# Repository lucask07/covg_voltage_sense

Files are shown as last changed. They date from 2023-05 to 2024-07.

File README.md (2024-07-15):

# COVG Voltage Sense Board

This board is physically small so it can be housed in an enclosure on a micromanipulator. The board input is a BNC connector which is compatible with glass microelectrode holders. 

The input amplifier must have low capacitance to minimize the total filter from the capacitance and the microelectrode resistance. The first version has a fixed amplifier gain. 

The **Rev_b board** modifications were designed and implemented by undergraduate student Jordan Haag. The board incorporates programmable gain and uses a low-noise voltage reference, REF3440, as the reference input to the offset adjust DAC. The low-noise reference improves the noise performance of the system. 

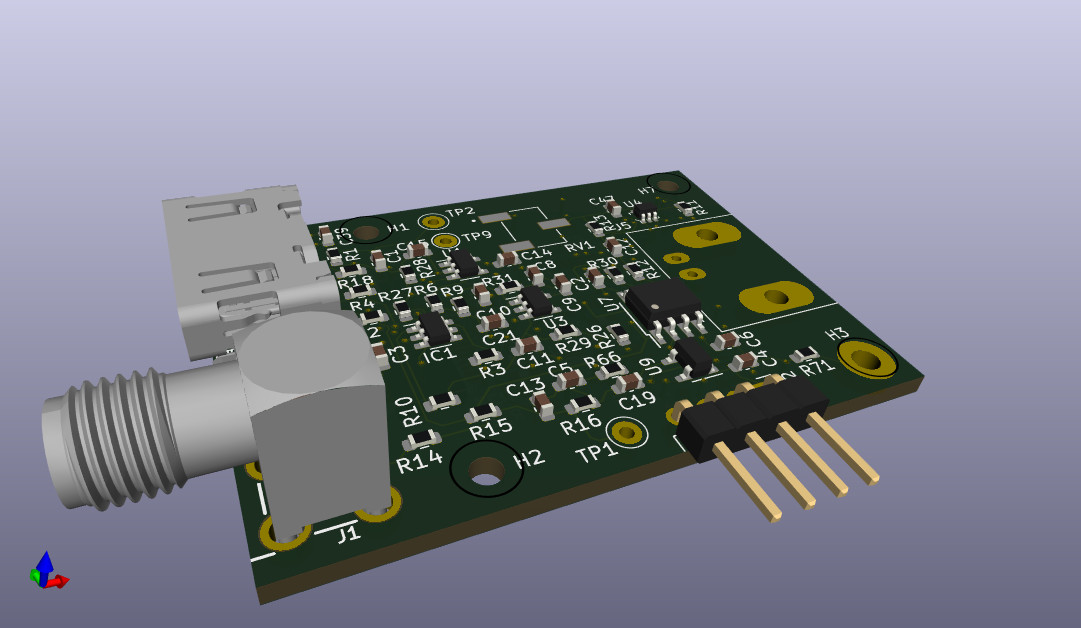
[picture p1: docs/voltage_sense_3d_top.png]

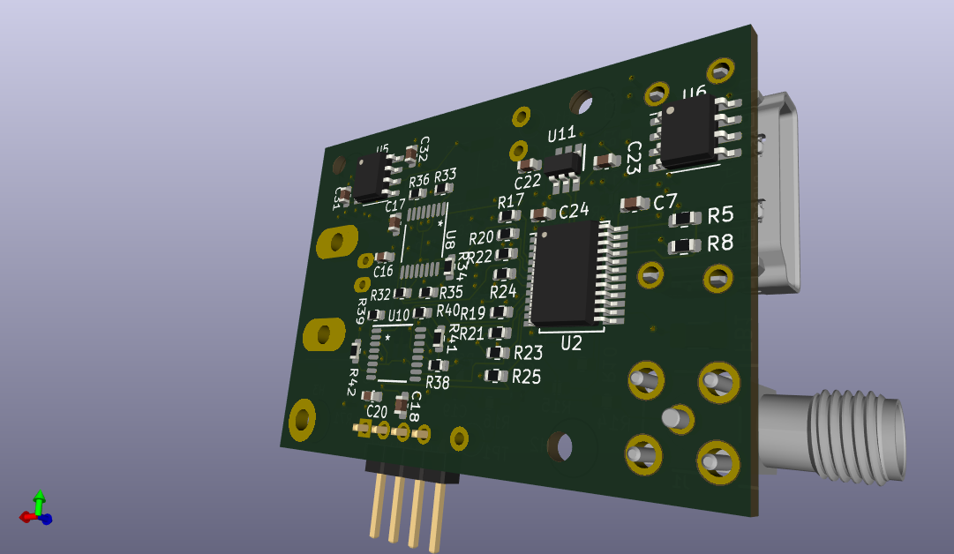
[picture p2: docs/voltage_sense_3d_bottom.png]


## Schematic
The [schematic](docs/voltage_sense.pdf) is in the DOCS folder.

## Fabrication
The second revision of this board was fabricated and assembled by JLCPCB. 

Order #: Y13-3276043A 

Assembly: SMT02402281623205-3276043A

Date: 2024/02/29

## Bill of Materials

The BOM is here JLCPCB assembly BOM 

Certain parts are not directly available from LCSC and so were pre-ordered. Pre-order: 24AA025UID, OPA1641,
DAC101C081CIMK/NOPB, TMUX6111PWR, TCA9555DBR, LP2981A-33DBVT, ADA4000-2ARZ-R7. Global sourcing: 3269W-1-103GLF, REF3440TIDBVR.

## Bugs and Future Improvement

* A footprint for a capacitor should be included in parallel with the feedback gain resistors, for example R33, R34, R35, and R36. This limits the amplifier bandwidth. Currently we work around this omission by stacking a capacitor on top of the resistor. Issue ([#4][i4])

[i4]: https://github.com/lucask07/covg_voltage_sense/issues/4

* U8,U10 (TMUX6111) and U11 (REF3440) were not assembled by JLCPCB and were lated added by hand.

## Upgrades 

This version addresses the following issues that occured with V1 

* DAC reference noise: https://github.com/lucask07/covg_voltage_sense/issues/5
* Negative capacitance connection: https://github.com/lucask07/covg_voltage_sense/issues/3
* C8 causes oscillation: https://github.com/lucask07/covg_voltage_sense/issues/2
* Incorrect BOM resistor values: https://github.com/lucask07/covg_voltage_sense/issues/1

## Miscellaneous

### HDMI: connection from DAQ to daughtercard 

The digital COVG project uses the concept of one main data acquisition board connected to an FPGA. The main data acquisition board has multiple channels that extend to daughtercards. The connection to each daughtercard allows for low-latency control by connections to high-speed ADCs and DACs on the daq board. For COVG the daughtercards are the bath clamp; the guard clamp; the voltage clamp and I force; and the V1/V2. The connectivity to the daughtercard is generalized and will be the same for each. 

An HDMI-A cable is used for input and output signals that connect the bath clamp daughtercard to the DAQ board. The HDMI cable carries:

- **power**: +5V, +15V, -15V
- **GND** 
- **Analog outputs** (to ADCs): 
	- OUT\_P, OUT\_N differential pair (x1) to 5 MSPS ADC 
	- single-ended out AMP\_OUT, CAL\_ADC both to individual channel of 1 MSPS ADC (ADS8686) 
- **Analog reference**: VCM: buffered ADC common-mode voltage (nominal 2.5 V)
- **Digital inputs** (from DACs): 
	- CMD: (command signal) from 1 us settling time DAC (attenuated by x10 at board)
	- CC: (capacitive compensation) from 1 us settling time DAC. AC coupled. 
	- CAL_DAC: from 5 us settling time DAC (DAC8050). Either voltage source or current source (Howland current pump), programmable on DAQ board
- **Digital control** (I2C): SDA, SCL (@ 3.3 V levels). Pull-ups are on DAQ board not on the daughtercards! The daughtercards use a TCA9555 I/O expander to generate many control signals from the I2C interface. 
- **Utiility** grab-bag connected to test-point. Jumper on DAQ board to set to analog in, analog out or digital I/O.

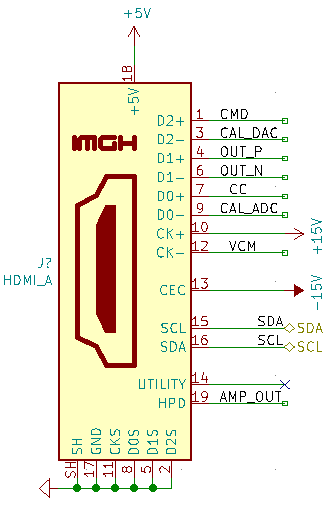
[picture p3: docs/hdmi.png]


| Pin | HDMI name    | Generic Daughtercard     | Bath clamp | Notes  |
|-----|--------------|--------------|------------|---------------------------------------------------------------------------|
| 1   | Data2+       | fastDAC1     | CMD        | ~1 us settling time                      |
| 2   | Data2 shield | Gnd          | Gnd        |                                                                           |
| 3   | Data2-       | Analog/GPIO1 | CAL_DAC    | Analog input signal from DAC8050, 16 bit, 5us settle, 5 V supply                                                                         |
| 4   | Data1+       | fastADC+     | IM_P       | to AD7960/AD7961. Differential low-pass filter on DAQ board                                                                          |
| 5   | Data1 shield | Gnd          | Gnd        |                                                                           |
| 6   | Data1-       | fastADC-     | IM_N       | to AD7960/AD7961. Differential low-pass filter on DAQ board                                                                          |
| 7   | Data0+       | fastDAC2     | CC         | ~1 us settling time                                                                          |
| 8   | Data0 shield | Gnd          | Gnd        |                                                                           |
| 9   | Data0-       | Analog/GPIO2 | CAL_ADC    | to ADS8686 1 MSPS, programmable PGA for range up to +/-10V                                                           |
| 10  | Clock+       | 15V          | 15V        | From a linear regulator on the DAQ board, 75 mA max per channel                                                                         |
| 11  | Clock shield | Gnd          | Gnd        |                                                                           |
| 12  | Clock-       | VCM          | VCM        | buffered on DAQ board, nominal 2.5 V                                                                          |
| 13  | CEC          | -15V         | -15V       | From a linear regulator on the DAQ board, 75 mA max per channel                             |
| 14  | Reserved     | open         | open       | Resistor jumper on DAQ board sets as analog in, analog out, or digital I/O (@ 3.3 V levels). Default stuffing option is to connect to the general purpose ADC (ADS8686). |
| 15  | SCL          | SCL          | SCL        | I2C clock. Pull-up on main DAQ board, 3.3 V levels                |
| 16  | SDA          | SDA          | SDA        | I2C data. Pull-up on main DAQ board, 3.3 V levels                 |
| 17  | Gnd          | Gnd          | Gnd        |                                                                           |
| 18  | 5V           | 5V           | 5V         | Power input from linear regulator, 200 mA max per channel (target)  |
| 19  | HPD          | Analog/GPIO3 | AMP_OUT    | output to ADS8686 1 MSPS, programmable PGA                        |

### Acknowledgments

Research reported in this repository was supported by the National Institute Of Neurological Disorders And Stroke of the National Institutes of Health under Award Number R15NS116907. The content is solely the responsibility of the authors and does not necessarily represent the official views of the National Institutes of Health.

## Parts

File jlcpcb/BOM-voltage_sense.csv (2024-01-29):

Comment | Designator | Footprint | LCSC
1n | C8 | C_0603_1608Metric | C100040
10p | C21 | C_0603_1608Metric | C106245
1u | C11,C23,C24 | C_0603_1608Metric | C106858
470k | R35,R41 | R_0603_1608Metric | C114622
33R | R14,R18 | R_0603_1608Metric | C13320
3k | R1,R11,R13,R16,R26,R30 | R_0603_1608Metric | C137732
OPA188xxDBV | U1,U3 | TSOT-23-5 | C140312
100k | R17,R19,R20,R21,R22,R23,R24,R25,R5 | R_0603_1608Metric | C14675
0.1u | C10,C14,C15,C16,C17,C18,C2,C20,C22,C3,C31,C32,C39,C4,C47,C6,C7,C9 | C_0603_1608Metric | C1591
10p | C12 | C_0603_1608Metric | C1634
Ferrite_Bead | FB1 | C_1206_3216Metric | C16902
24AA025UID | U6 | SOIC-8_3.9x4.9mm_P1.27mm | C194184
OPA1641 | U5 | SOIC-8_3.9x4.9mm_P1.27mm | C2057597
0R | R12,R71 | R_0603_1608Metric | C21189
348k | R34,R40 | R_0603_1608Metric | C227488
226k | R33,R39 | R_0603_1608Metric | C227714
30k | R15,R2 | R_0603_1608Metric | C22984
604k | R36,R42 | R_0603_1608Metric | C245986
1R | R66 | R_0603_1608Metric | C25212
Conn_Coaxial | J5 | BNC_Amphenol_B6252HB-NPP3G-50_Horizontal | C2837587
LP2981A-33DBVT | U9 | SOT-23-5 | C2872227
Conn_Coaxial | J1 | BU-SMA-G | C2874827
HDMI_A | J4 | CONN_10029449-111RLF_HDMI_A | C427307
MCP4017T-103E_LT | U4 | SOT-363 | C478095
4.7u | C5 | C_0603_1608Metric | C69335
49.9k | R10,R6 | R_0603_1608Metric | C705780
4.99k | R29,R9 | R_0603_1608Metric | C723532
49.9R | R31 | R_0603_1608Metric | C859049
10k | R27,R28,R3 | R_0603_1608Metric | C95204
DNI | R8 | R_0603_1608Metric
DNI | R4 | R_0603_1608Metric
DNI | H3 | MountingHole_2.2mm_M2_Pad
DNI | H7 | MountingHole_2.2mm_M2
DNI | J2 | PinHeader_1x04_P2.54mm_Horizontal
TCA9555DBR | U2 | SSOP-24_5.3x8.2mm_P0.65mm
DNI | C1 | C_0603_1608Metric
RCT-0C | TP1,TP2 | Test_Point_D1.02mm
DNI | C19 | C_0603_1608Metric
DAC101C081CIMK_NOPB | IC1 | TSOT-23-6
DNI | TP9 | TestPoint_THTPad_D2.0mm_Drill1.0mm
DNI | H1 | MountingHole_2.2mm_M2
10k pot | RV1 | TRIM_3269W-1-103GLF
DNI | C13 | C_0603_1608Metric
DNI | H2 | MountingHole_2.2mm_M2
ADA4000-2ARZ-R7 | U7 | R_8_ADI
TMUX6111PWR | U10 | PW0016A_N
DNI | R32 | R_0603_1608Metric
DNI | R38 | R_0603_1608Metric
TMUX6111PWR | U8 | PW0016A_N
REF3440TIDBVR | U11 | REF3440

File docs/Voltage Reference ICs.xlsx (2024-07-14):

Package | Manf # | DigiKey # | Price ($) | Quantity in Stock | LCSC Stock? | Noise Voltage at 10 Hz(uV p-p) | Noise Voltage at 10k Hz(uV p-p) | Accuracy (%) | Notes
SOT-6 | MAX6071BAUT41+T | MAX6071BAUT41+TCT-ND | 3 | 11000 | N | 9.6 | 34 | 0.08 | pin compatible w/same bypass caps
SOT-6 | REF3440TIDBVR | 296-REF3440TIDBVRCT-ND | 2.54 | 1800 | N | 3.8 | 48 | 0.05 | pin compatible w/same bypass caps
8-SO | LTC1798CS8-4.1#PBF | 505-LTC1798CS8-4.1#PBF-ND | 6.37 | 100 | N | 8 | - | 0.15 | not pin compatible
8-SOIC | LM4140BCM-4.1/NOPB | LM4140BCM-4.1/NOPB-ND | 5.77 | 540 | N | 2.2 | - | 0.1 | not pin compatible
8-VSSOP | REF3440QDGKRQ1 | 296-REF3440QDGKRQ1CT-ND | 3.8 | 2500 | N | 3.8 | 48 | 0.05 | not pin compatible
8-MSOP | LTC1258CMS8-4.1#PBF | 505-LTC1258CMS8-4.1#PBF-ND | 7.28 | 110 | N | 8 | - | 0.18 | not pin compatible
8-MSOP | ADR444ARMZ-REEL7 | 505-ADR444ARMZ-REEL7CT-ND | 8.37 | 1200 | Y | 1.8 | - | 0.13 | not pin compatible

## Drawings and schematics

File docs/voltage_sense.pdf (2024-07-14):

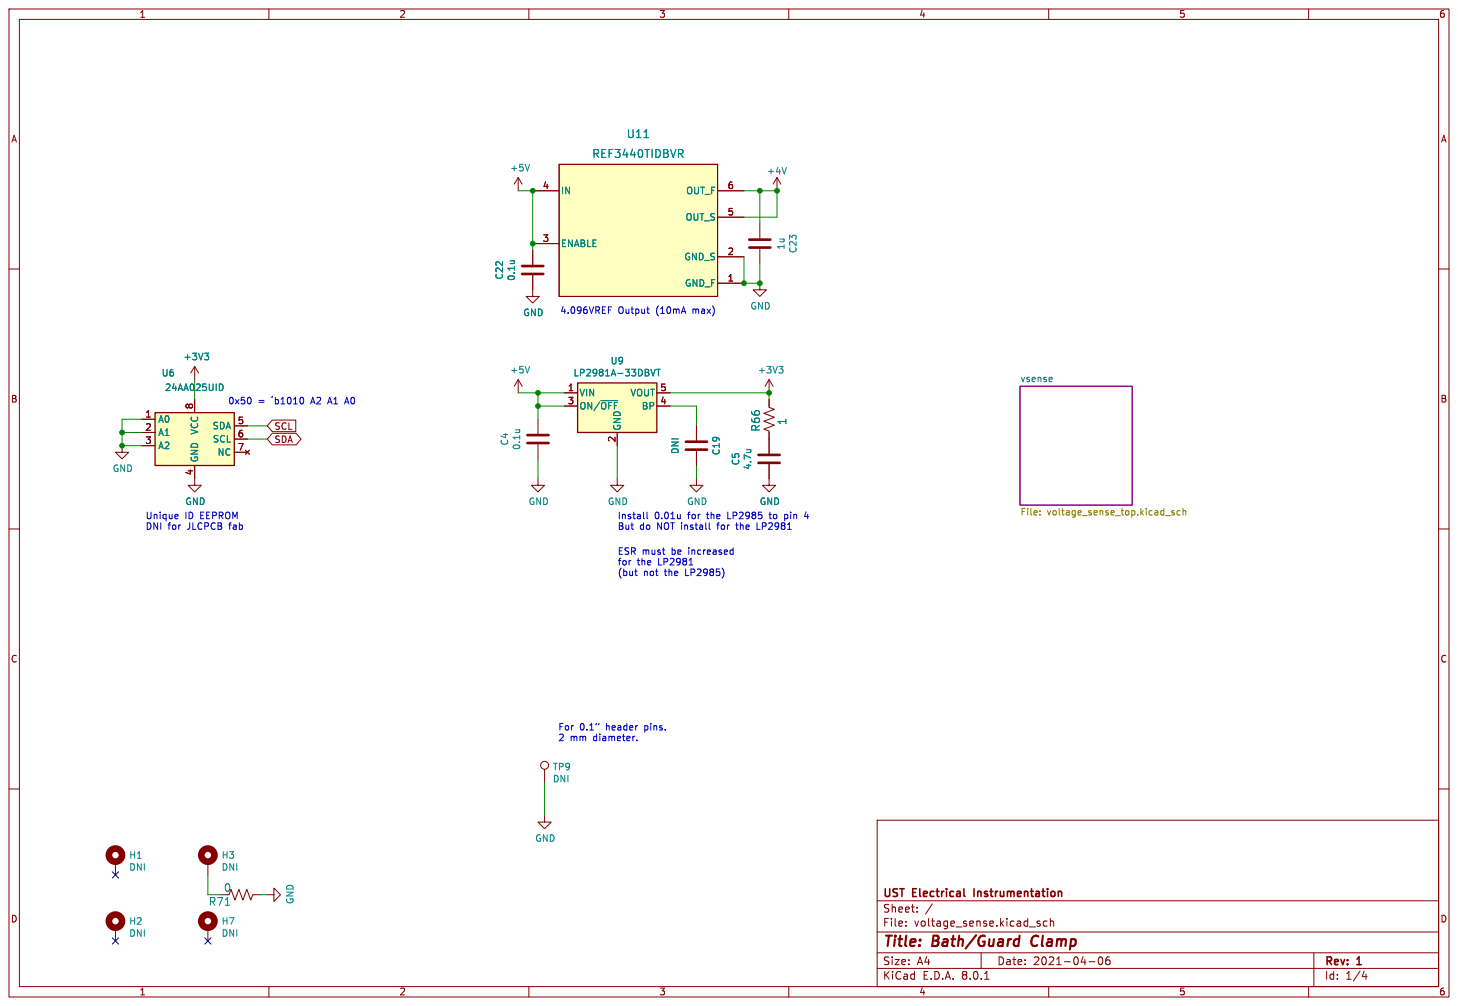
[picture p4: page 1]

24AA025UID
(but not the LP2985) For þÿ0.1  header pins. 2 mm diameter. 0x50 = þÿ b1010 A2 A1 A0 Unique ID EEPROM

2 ON/~{OFF} 3 BP 4 VOUT 5 U9
+3V3 GND

2 ON/~{OFF} 3 BP 4 VOUT 5

4 SDA 5 SCL 6 NC 7 VCC

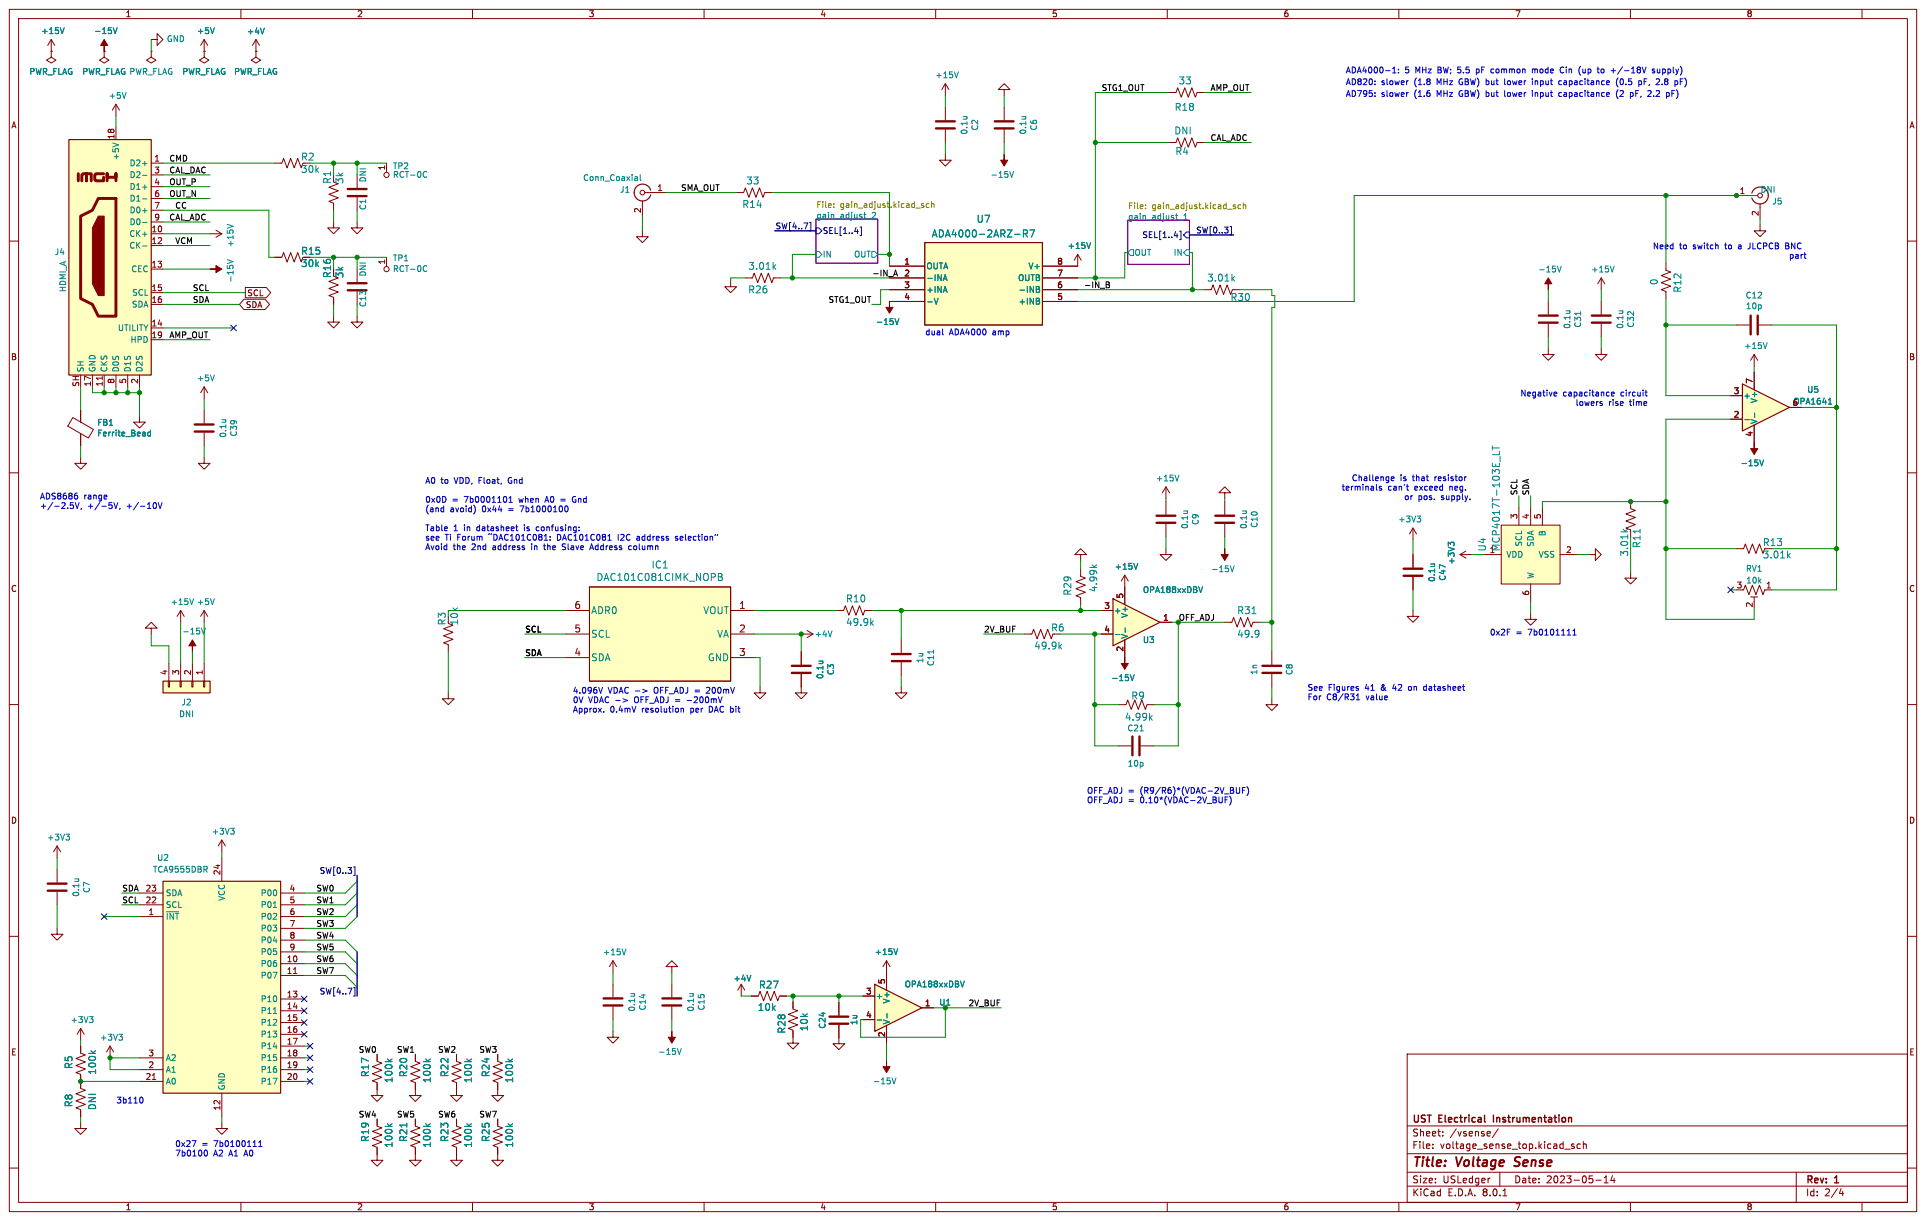
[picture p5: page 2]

Need to switch to a JLCPCB BNC

0x2F = 7b0101111 OFF_ADJ = (R9/R6)*(VDAC-2V_BUF) OFF_ADJ = 0.10*(VDAC-2V_BUF) A0 to VDD, Float, Gnd

Id: 2/4 Title: Voltage Sense

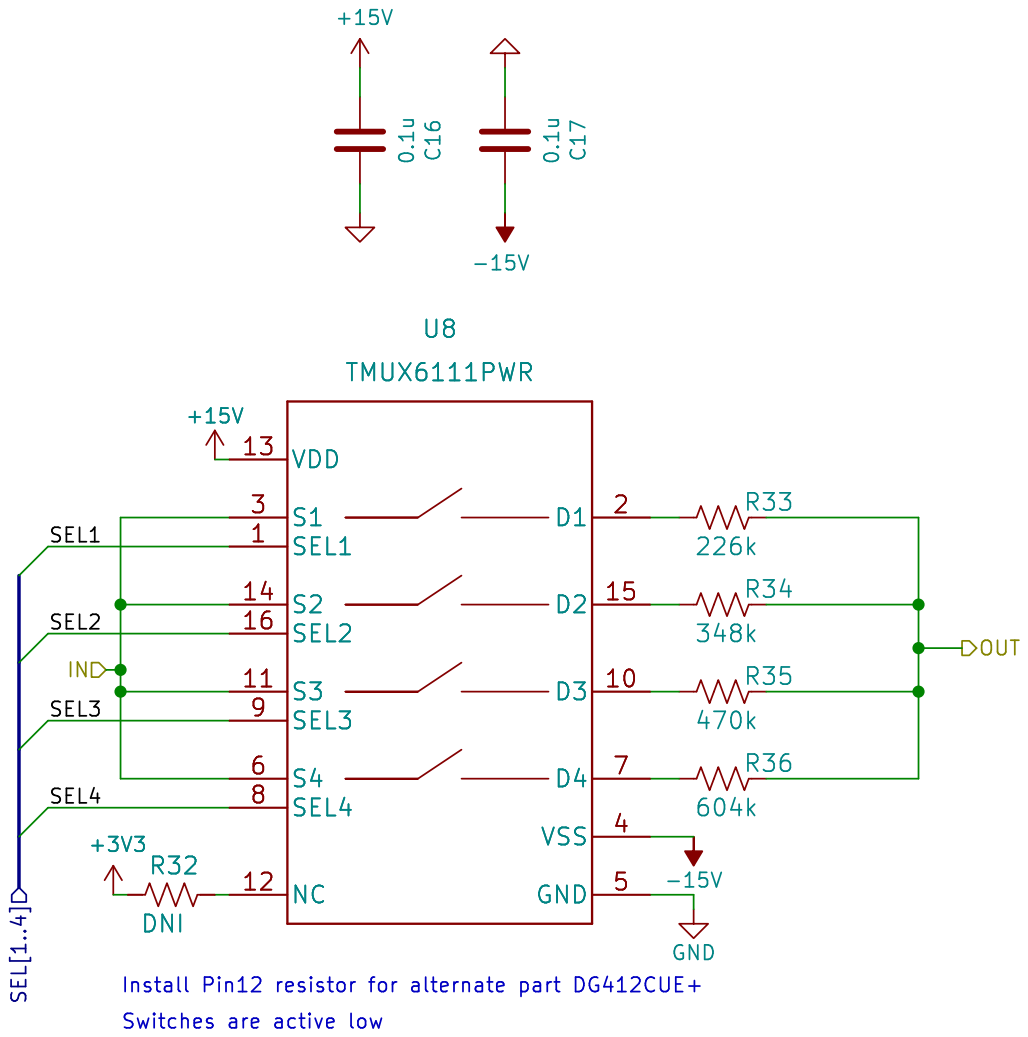
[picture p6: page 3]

Id: 3/4 Title: File: gain_adjust.kicad_sch Sheet: /vsense/gain_adjust_1/

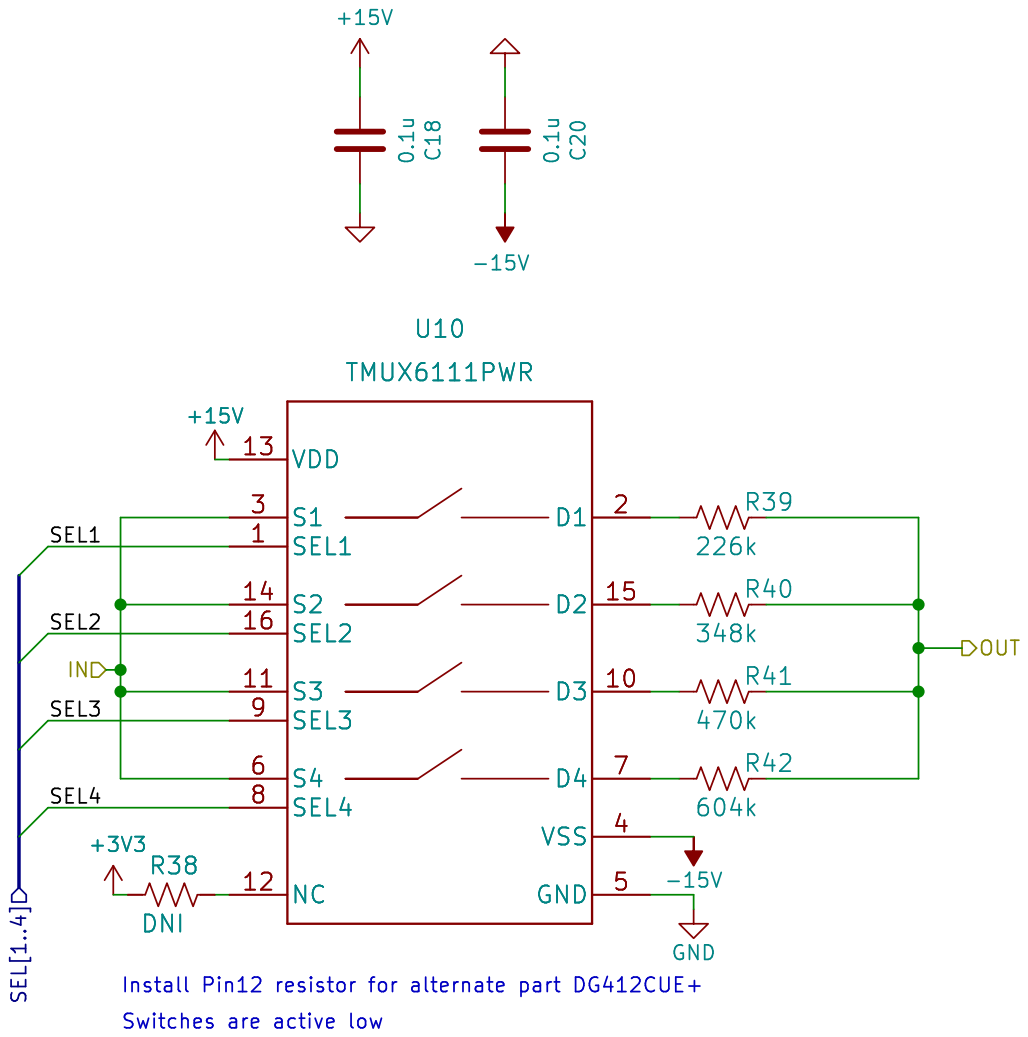
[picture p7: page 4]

Id: 4/4 Title: File: gain_adjust.kicad_sch Sheet: /vsense/gain_adjust_2/

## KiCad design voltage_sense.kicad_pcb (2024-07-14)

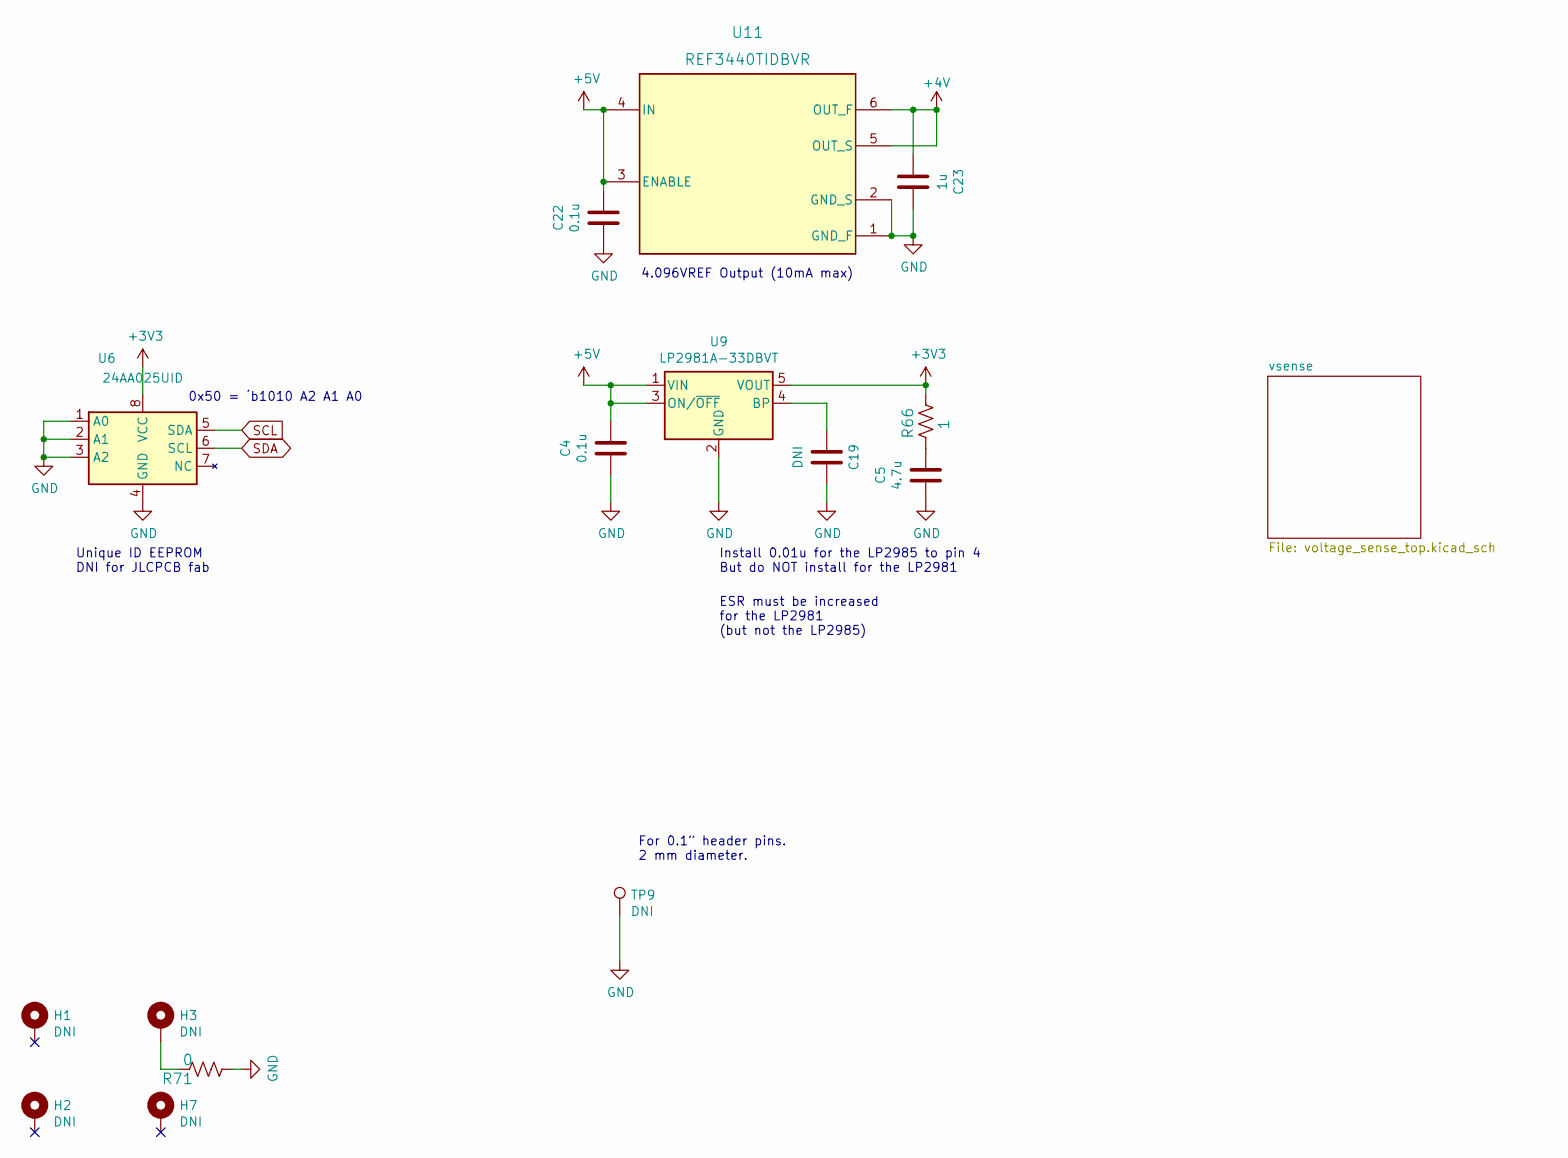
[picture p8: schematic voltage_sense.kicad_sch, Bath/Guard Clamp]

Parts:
C4, C22: 0.1u; C_0603_1608Metric; Tolerance 10%; voltage 25V
C5: 4.7u; C_0603_1608Metric; Tolerance 20%; voltage 25V
C19: DNI; C_0603_1608Metric
C23: 1u; C_0603_1608Metric; Tolerance 20%; voltage 25V
H1, H2, H7: DNI; MountingHole_2.2mm_M2
H3: DNI; MountingHole_2.2mm_M2_Pad
R66: 1; R_0603_1608Metric; Tolerance 1%
R71: 0; R_0603_1608Metric; Tolerance 1%
TP9: DNI; TestPoint_THTPad_D2.0mm_Drill1.0mm
U6: 24AA025UID; SOIC-8_3.9x4.9mm_P1.27mm
U9: LP2981A-33DBVT; SOT-23-5
U11: REF3440TIDBVR; REF3440

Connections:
+3V3: R66.1, U6.8 (VCC), U9.5 (VOUT); also elsewhere on the board
+4V: C23.2, U11.5 (OUT_S), U11.6 (OUT_F); also elsewhere on the board
+5V: C4.1, C22.1, U9.1 (VIN), U9.3 (ON/~OFF), U11.3 (ENABLE), U11.4 (IN); also elsewhere on the board
GND: C4.2, C5.2, C19.2, C22.2, C23.1, R71.2, TP9.1, U6.1 (A0), U6.2 (A1), U6.3 (A2), U6.4 (GND), U9.2 (GND), U11.1 (GND_F), U11.2 (GND_S); also elsewhere on the board
unnamed: C5.1, R66.2
unnamed: C19.1, U9.4 (BP)
unnamed: H3.1, R71.1
SCL: U6.5 (SDA); also elsewhere on the board
SDA: U6.6 (SCL); also elsewhere on the board

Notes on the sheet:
For 0.1” header pins. 2 mm diameter.
Install 0.01u for the LP2985 to pin 4 But do NOT install for the LP2981
Unique ID EEPROM DNI for JLCPCB fab
0x50 = ‘b1010 A2 A1 A0
4.096VREF Output (10mA max)
ESR must be increased for the LP2981 (but not the LP2985)

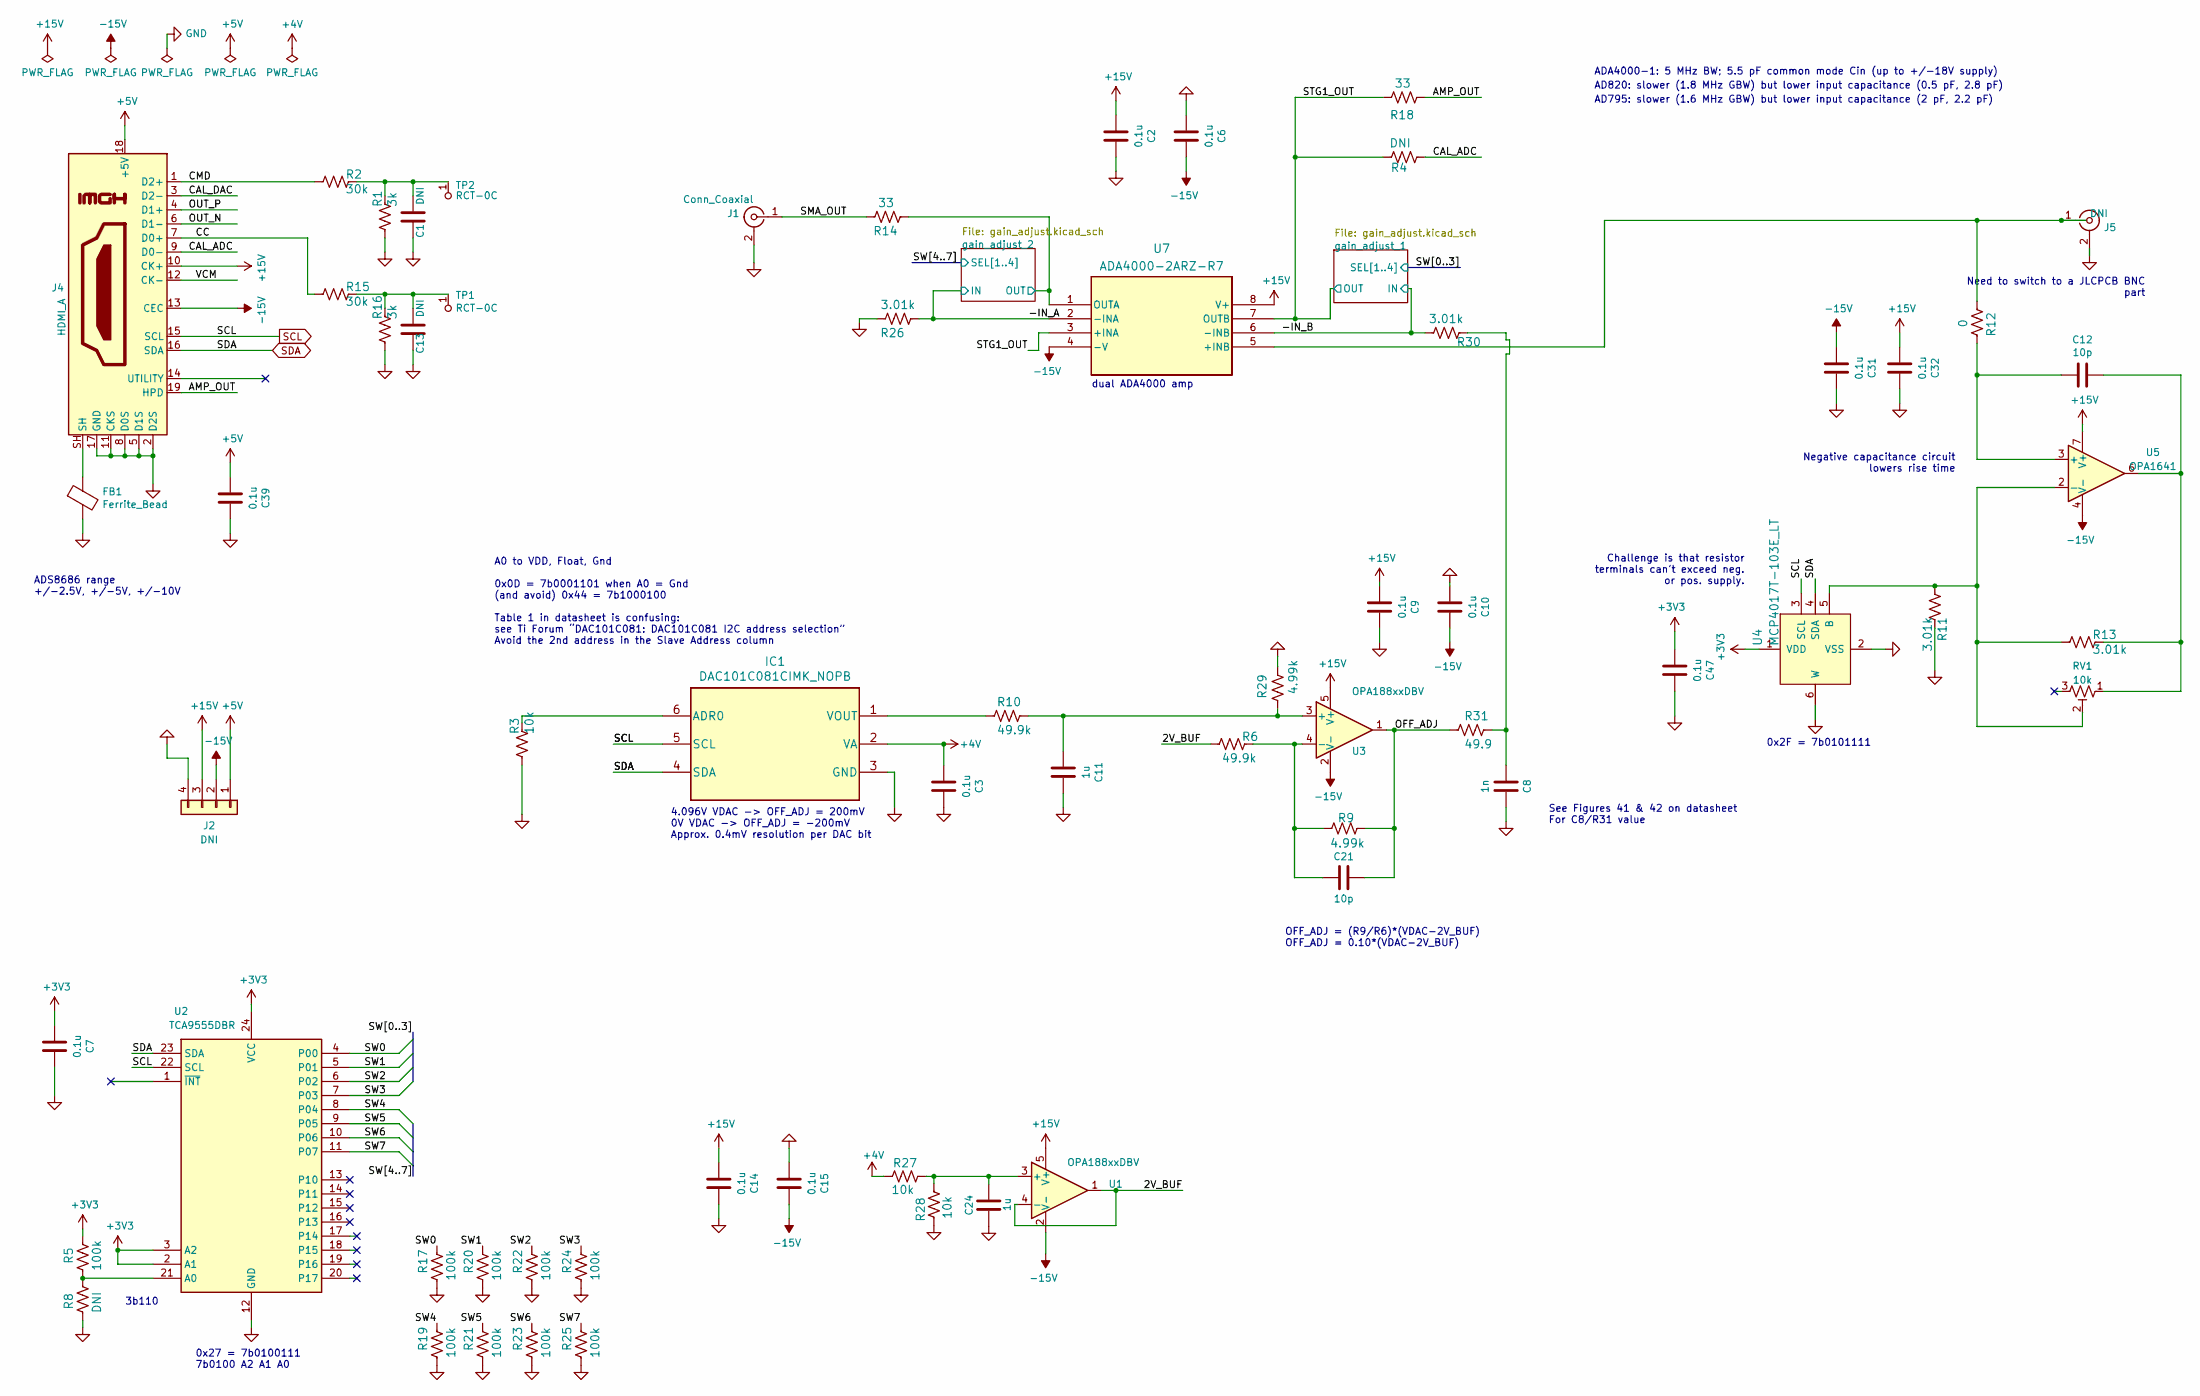
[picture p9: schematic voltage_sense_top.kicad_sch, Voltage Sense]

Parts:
C1, C13: DNI; C_0603_1608Metric; Tolerance 5%; voltage 50V
C2, C3, C6, C9, C10, C14, C15, C31, C39: 0.1u; C_0603_1608Metric; Tolerance 20%; voltage 25V
C7, C32, C47: 0.1u; C_0603_1608Metric; voltage 25V
C8: 1n; C_0603_1608Metric; Tolerance 20%; voltage 25V
C11, C24: 1u; C_0603_1608Metric; Tolerance 20%; voltage 25V
C12: 10p; C_0603_1608Metric; Tolerance 5%
C21: 10p; C_0603_1608Metric; Tolerance 20%; voltage 25V
FB1: Ferrite_Bead; C_1206_3216Metric
IC1: DAC101C081CIMK_NOPB; TSOT-23-6
J1: Conn_Coaxial; BU-SMA-G
J2: DNI; PinHeader_1x04_P2.54mm_Horizontal
J4: HDMI_A; CONN_10029449-111RLF_HDMI_A
J5: DNI; BNC_Amphenol_B6252HB-NPP3G-50_Horizontal
R1, R16: 3k; R_0603_1608Metric; Tolerance 1%
R2, R15: 30k; R_0603_1608Metric; Tolerance 1%
R3: 10k; R_0603_1608Metric; Tolerance 5%
R4, R8: DNI; R_0603_1608Metric; Tolerance 1%
R5, R17, R19, R20, R21, R22, R23, R24, R25: 100k; R_0603_1608Metric; Tolerance 1%
R6, R10: 49.9k; R_0603_1608Metric; Tolerance 1%
R9, R29: 4.99k; R_0603_1608Metric; Tolerance 1%
R11, R13, R26, R30: 3.01k; R_0603_1608Metric; Tolerance 1%
R12: 0; R_0603_1608Metric; Tolerance 1%
R14, R18: 33; R_0603_1608Metric; Tolerance 1%
R27, R28: 10k; R_0603_1608Metric; Tolerance 1%
R31: 49.9; R_0603_1608Metric; Tolerance 1%
RV1: 10k; TRIM_3269W-1-103GLF
TP1, TP2: RCT-0C; Test_Point_D1.02mm
U1, U3: OPA188xxDBV; TSOT-23-5
U2: TCA9555DBR; SSOP-24_5.3x8.2mm_P0.65mm
U4: MCP4017T-103E_LT; SOT-363; MPN MCP4017T-103E/LT; Digi-Key_PN MCP4017T-103E/LTCT-ND
U5: OPA1641; SOIC-8_3.9x4.9mm_P1.27mm
U7: ADA4000-2ARZ-R7; R_8_ADI

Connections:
+3V3: C7.2, C47.2, R5.1, U2.2 (A1), U2.3 (A2), U2.24 (VCC), U4.1 (VDD); also elsewhere on the board
+4V: C3.2, IC1.2 (VA), R27.2; also elsewhere on the board
+5V: C39.2, J2.1, J4.18 (+5V); also elsewhere on the board
+15V: C2.2, C9.2, C14.2, C32.2, J2.3, J4.10 (CK+), U1.5 (V+), U3.5 (V+), U5.7 (V+), U7.8 (V+); also elsewhere on the board
-15V: C6.1, C10.1, C15.1, C31.2, J2.2, J4.13 (CEC), U1.2 (V-), U3.2 (V-), U5.4 (V-), U7.4 (-V); also elsewhere on the board
/vsense/2V_BUF: R6.2, U1.1, U1.4 (-)
/vsense/-IN_A: R26.2, U7.2 (-INA); also elsewhere on the board
/vsense/-IN_B: R30.1, U7.6 (-INB); also elsewhere on the board
/vsense/AMP_OUT: J4.19 (HPD), R18.2
/vsense/CAL_ADC: J4.9 (D0-), R4.2
/vsense/CAL_DAC: J4.3 (D2-)
/vsense/CC: J4.7 (D0+), R15.2
/vsense/CMD: J4.1 (D2+), R2.2
/vsense/OFF_ADJ: C21.1, R9.1, R31.2, U3.1
/vsense/OUT_N: J4.6 (D1-)
/vsense/OUT_P: J4.4 (D1+)
/vsense/SMA_OUT: J1.1 (In), R14.1
/vsense/STG1_OUT: R4.1, R18.1, U7.3 (+INA), U7.7 (OUTB); also elsewhere on the board
/vsense/SW0: R17.1, U2.4 (P00); also elsewhere on the board
/vsense/SW1: R20.1, U2.5 (P01); also elsewhere on the board
/vsense/SW2: R22.1, U2.6 (P02); also elsewhere on the board
/vsense/SW3: R24.1, U2.7 (P03); also elsewhere on the board
/vsense/SW4: R19.1, U2.8 (P04); also elsewhere on the board
/vsense/SW5: R21.1, U2.9 (P05); also elsewhere on the board
/vsense/SW6: R23.1, U2.10 (P06); also elsewhere on the board
/vsense/SW7: R25.1, U2.11 (P07); also elsewhere on the board
/vsense/VCM: J4.12 (CK-)
/vsense/gain_adjust_2/OUT: R14.2, U7.1 (OUTA); also elsewhere on the board
GND: C1.1, C2.1, C3.1, C6.2, C7.1, C8.1, C9.1, C10.2, C11.1, C13.1, C14.1, C15.2, C24.1, C31.1, C32.1, C39.1, C47.1, FB1.2, IC1.3 (GND), J1.2 (Ext), J2.4, J4.2 (D2S), J4.5 (D1S), J4.8 (D0S), J4.11 (CKS), J4.17 (GND), J5.2 (Ext), R1.2, R3.2, R8.2, R11.1, R16.2, R17.2, R19.2, R20.2, R21.2, R22.2, R23.2, R24.2, R25.2, R26.1, R28.2, R29.1, U2.12 (GND), U4.2 (VSS), U4.6 (W); also elsewhere on the board
unnamed: C1.2, R1.1, R2.1, TP2.1
unnamed: C8.2, R30.2, R31.1
unnamed: C11.2, R10.1, R29.2, U3.3 (+)
unnamed: C12.1, R13.1, RV1.1, U5.6
unnamed: C12.2, R12.1, U5.3 (+)
unnamed: C13.2, R15.1, R16.1, TP1.1
unnamed: C21.2, R6.1, R9.2, U3.4 (-)
unnamed: C24.2, R27.1, R28.1, U1.3 (+)
unnamed: FB1.1, J4.SH
unnamed: IC1.1 (VOUT), R10.2
unnamed: IC1.6 (ADR0), R3.1
unnamed: J5.1 (In), R12.2, U7.5 (+INB)
unnamed: R5.2, R8.1, U2.21 (A0)
unnamed: R11.2, R13.2, RV1.2, U4.5 (B), U5.2 (-)
SCL: IC1.5 (SCL), J4.15 (SCL), U2.22 (SCL), U4.3 (SCL); also elsewhere on the board
SDA: IC1.4 (SDA), J4.16 (SDA), U2.23 (SDA), U4.4 (SDA); also elsewhere on the board

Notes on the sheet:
0x27 = 7b0100111 7b0100 A2 A1 A0
AD795: slower (1.6 MHz GBW) but lower input capacitance (2 pF, 2.2 pF)
Negative capacitance circuit lowers rise time
Challenge is that resistor terminals can't exceed neg. or pos. supply.
4.096V VDAC -> OFF_ADJ = 200mV 0V VDAC -> OFF_ADJ = -200mV Approx. 0.4mV resolution per DAC bit
dual ADA4000 amp
0x2F = 7b0101111
OFF_ADJ = (R9/R6)*(VDAC-2V_BUF) OFF_ADJ = 0.10*(VDAC-2V_BUF)
ADS8686 range +/-2.5V, +/-5V, +/-10V
AD820: slower (1.8 MHz GBW) but lower input capacitance (0.5 pF, 2.8 pF)
See Figures 41 & 42 on datasheet For C8/R31 value
A0 to VDD, Float, Gnd 0x0D = 7b0001101 when A0 = Gnd (and avoid) 0x44 = 7b1000100 Table 1 in datasheet is confusing: see Ti Forum “DAC101C081: DAC101C081 I2C address selection” Avoid the 2nd address in the Slave Address column
3b110
Need to switch to a JLCPCB BNC part
ADA4000-1: 5 MHz BW; 5.5 pF common mode Cin (up to +/-18V supply)

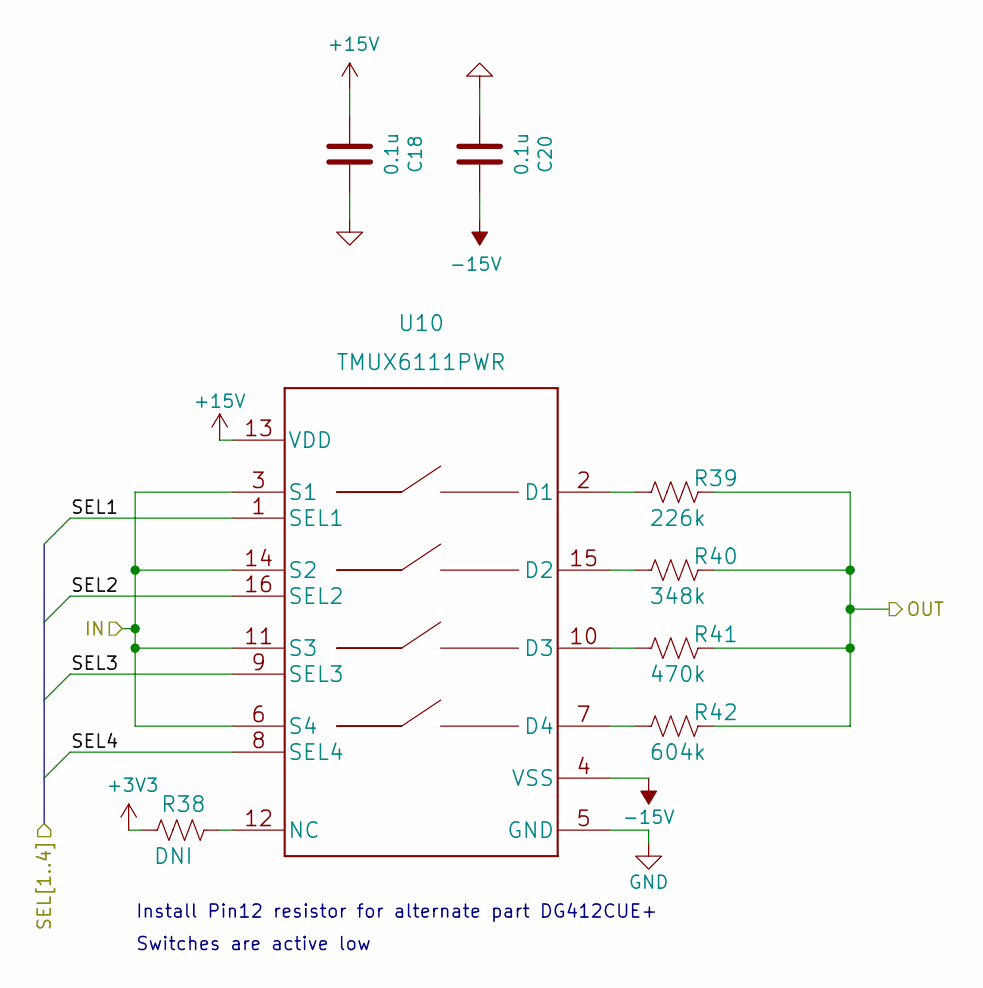
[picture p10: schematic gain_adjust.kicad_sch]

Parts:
C18, C20: 0.1u; C_0603_1608Metric; Tolerance 20%; voltage 25V
R38: DNI; R_0603_1608Metric; Tolerance 1%
R39: 226k; R_0603_1608Metric; Tolerance 1%
R40: 348k; R_0603_1608Metric; Tolerance 1%
R41: 470k; R_0603_1608Metric; Tolerance 1%
R42: 604k; R_0603_1608Metric; Tolerance 1%
U10: TMUX6111PWR; PW0016A_N

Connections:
+3V3: R38.1; also elsewhere on the board
+15V: C18.2, U10.13 (VDD); also elsewhere on the board
-15V: C20.1, U10.4 (VSS); also elsewhere on the board
/vsense/-IN_A: U10.3 (S1), U10.6 (S4), U10.11 (S3), U10.14 (S2); also elsewhere on the board
/vsense/SW4: U10.1 (SEL1); also elsewhere on the board
/vsense/SW5: U10.16 (SEL2); also elsewhere on the board
/vsense/SW6: U10.9 (SEL3); also elsewhere on the board
/vsense/SW7: U10.8 (SEL4); also elsewhere on the board
/vsense/gain_adjust_2/OUT: R39.1, R40.1, R41.1, R42.1; also elsewhere on the board
GND: C18.1, C20.2, U10.5 (GND); also elsewhere on the board
unnamed: R38.2, U10.12 (NC)
unnamed: R39.2, U10.2 (D1)
unnamed: R40.2, U10.15 (D2)
unnamed: R41.2, U10.10 (D3)
unnamed: R42.2, U10.7 (D4)

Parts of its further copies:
C16, C17: 0.1u; C_0603_1608Metric; Tolerance 20%; voltage 25V
R32: DNI; R_0603_1608Metric; Tolerance 1%
R33: 226k; R_0603_1608Metric; Tolerance 1%
R34: 348k; R_0603_1608Metric; Tolerance 1%
R35: 470k; R_0603_1608Metric; Tolerance 1%
R36: 604k; R_0603_1608Metric; Tolerance 1%
U8: TMUX6111PWR; PW0016A_N

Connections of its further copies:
+3V3: R32.1; also elsewhere on the board
+15V: C16.2, U8.13 (VDD); also elsewhere on the board
-15V: C17.1, U8.4 (VSS); also elsewhere on the board
/vsense/-IN_B: U8.3 (S1), U8.6 (S4), U8.11 (S3), U8.14 (S2); also elsewhere on the board
/vsense/STG1_OUT: R33.1, R34.1, R35.1, R36.1; also elsewhere on the board
/vsense/SW0: U8.1 (SEL1); also elsewhere on the board
/vsense/SW1: U8.16 (SEL2); also elsewhere on the board
/vsense/SW2: U8.9 (SEL3); also elsewhere on the board
/vsense/SW3: U8.8 (SEL4); also elsewhere on the board
GND: C16.1, C17.2, U8.5 (GND); also elsewhere on the board
unnamed: R32.2, U8.12 (NC)
unnamed: R33.2, U8.2 (D1)
unnamed: R34.2, U8.15 (D2)
unnamed: R35.2, U8.10 (D3)
unnamed: R36.2, U8.7 (D4)

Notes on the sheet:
Install Pin12 resistor for alternate part DG412CUE+
Switches are active low

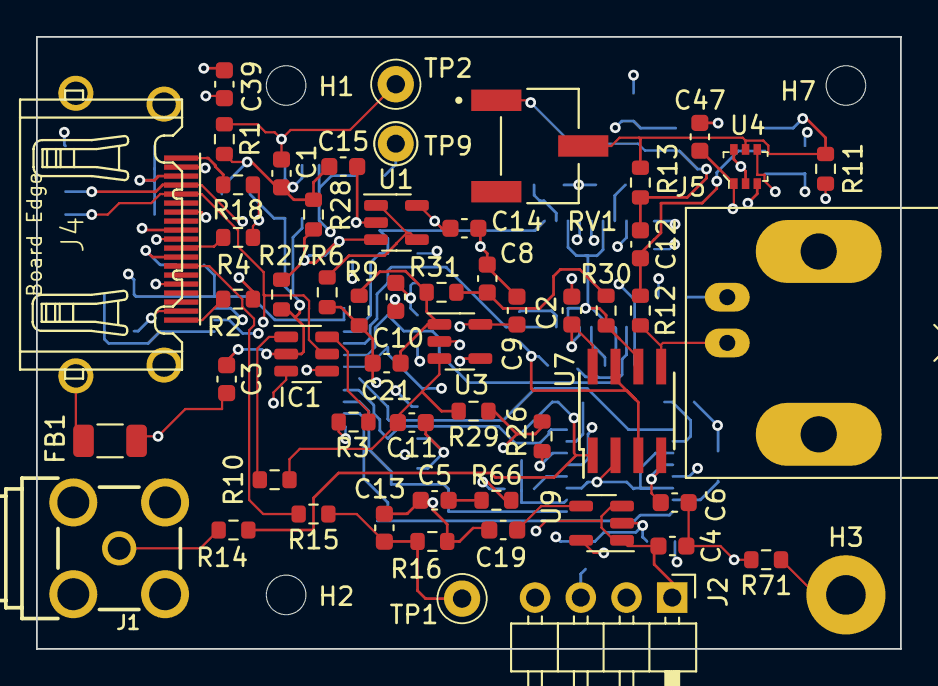
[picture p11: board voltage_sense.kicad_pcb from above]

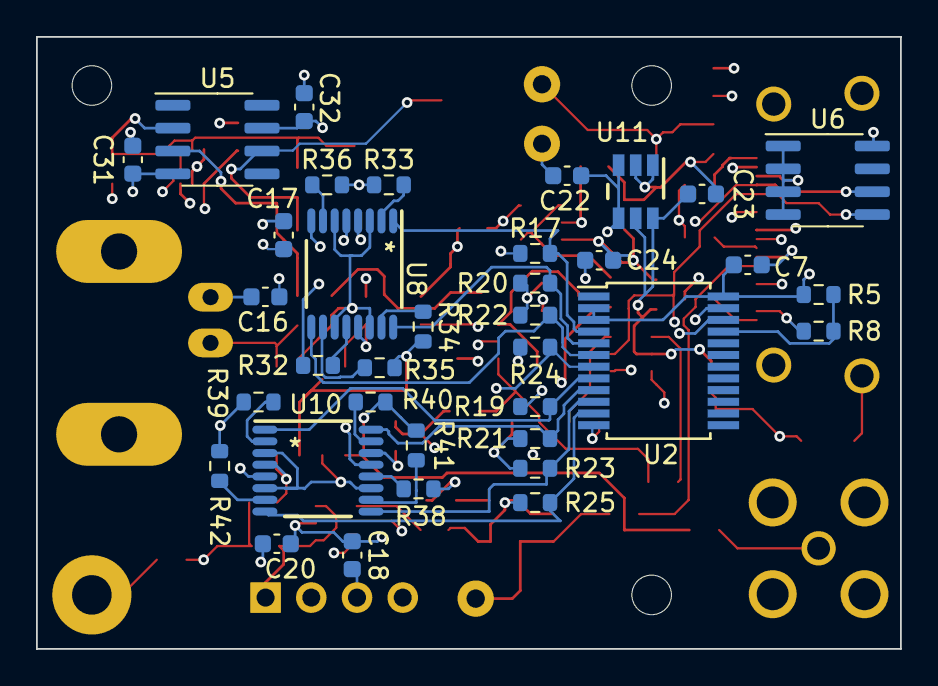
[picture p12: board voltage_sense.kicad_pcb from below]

Board: 6 copper layers, 48.0 x 34.0 mm, 95 parts (36 on the bottom side), 54 nets.

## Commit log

2023-05-17 found LCSC alternatives for some parts
    [voltage_sense.kicad_pcb, voltage_sense.kicad_sch, voltage_sense_top.kicad_sch]
2023-05-17 first draft of production files
    [BOM-voltage_sense.csv, CPL-voltage_sense.csv, bom.csv, designators.csv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]
2023-05-29 moved SMA to same size as HDMI
    [BOM-voltage_sense.csv, CPL-voltage_sense.csv, voltage_sense-CuBottom.gbr, voltage_sense-CuIn1.gbr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]
2023-05-29 files sent to JLCPCB; Order Y10-3276043A, SMT02305291257986-3276043A
    [CPL-voltage_sense.csv, voltage_sense-CuBottom.gbr, voltage_sense-CuIn1.gbr, voltage_sense-CuIn2.gbr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]
2024-02-01 add gerbers to jlcpcb
    [voltage_sense-CuBottom.gbr, voltage_sense-CuIn1.gbr, voltage_sense-CuIn2.gbr, voltage_sense-CuIn3.gbr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]
2024-02-27 All production files in jlcpcb/production_files
    [BOM-voltage_sense.csv, CPL-voltage_sense.csv, bom.csv, designators.csv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]
2024-07-14 add modified production files; schematic update by KiCAD version to 8.0.1
    [BOM-voltage_sense.csv, CPL-voltage_sense.csv, gain_adjust.kicad_sch, voltage_sense.kicad_pcb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]
2024-07-14 add Gain calculations from main branch
    [Gain Calculations.xlsx]
2024-07-14 add schematic plot to the docs folder
    [voltage_sense.kicad_pcb, voltage_sense_bom.csv]
2024-07-14 updates to README to include assembly info
    [Voltage Reference ICs.xlsx, voltage_sense.kicad_pcb]
